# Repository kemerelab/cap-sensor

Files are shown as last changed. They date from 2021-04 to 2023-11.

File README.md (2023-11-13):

# Capacitive sensor
## Theory
Capacitive sensing relies on, as the name suggests, the capacitance of the involved circuit. Capacitance, in turn, is the ability to store electrical charge under an applied voltage, which is employed by components termed capacitors. Clasically, capacitors can be visualized as two conductor plates separated by some distance $d$; the capacitance of these "parallel plate capacitors" is then governed by the equation:

$$
\displaystyle
C = \dfrac{Q}{V} = \epsilon \dfrac{A}{d}
$$

where $Q$ is the electrical charge stored on conductor plate; $V$ is the voltage applied to the capacitor; $\epsilon$ is the dielectric constant of the medium separating the plates; $A$ is the area of each plate; and $d$ is the distance between the plates.

Once charged after application of a voltage across the conductor plates (by, for example, a battery), the capacitor will similarly discharge across another component of a circuit if provided the opportunity. For example, consider the simple RC circuit below.

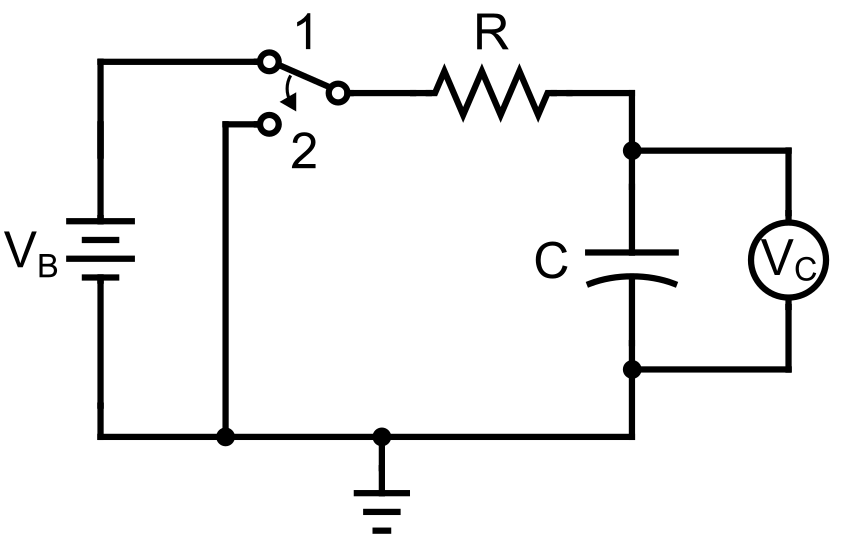
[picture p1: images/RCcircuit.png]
A simple RC circuit.


When connected to the battery, the capacitor with capacitance $C$ will store an amount of charge $Q$ after equilibrating at the battery voltage $V_B$ (position 1). If the circuit is disconnected from the battery (position 2), then an electric current will flow from the positively charged capacitor plate across the resistor to ground. The time-dependent voltage across the capacitor, $V_C$ follows a well-known exponential decay:

$$
\displaystyle
V(t) = V_B e^{-\frac{t}{\tau}}
$$

where $\tau = RC$ is known as the time constant of the circuit and is given by the product of the resistance and capacitance. (Similarly, reflecting the equation across the time axis gives the time-dependence for charging the capacitor.)

Lastly, it can be shown that for capacitors placed in parallel in an electrical circuit, the capacitance of the circuit is the sum of the individual capacitances of each capacitor:

$$
\displaystyle
C_{tot} = C_1 + C_2 + \cdots + C_n
$$

In other words, capacitance is additive in parallel.

How do these principles apply to capacitive sensing? Let's suppose that we have the RC circuit similar to the one above, except that we have an additional wire that connects the positive terminal to a conductive plate (i.e. one-half of a parallel plate capacitor). As some object object, say a finger, approaches this plate, it can form the other (negative) plate to generate an additional parallel plate capacitor. Moreover, if this object is connected to a large electrical reservoir, like a human body, it is in effect "virtually grounded", which functionally acts as if connected to the circuit ground, and thereby makes the new capacitor lie in parallel with the known capacitor. Consequently, because capacitance adds in parallel, the new capacitance of the circuit will have increased. (The exact amount is not important, as we will see.) (If placed directly between the plates of a large capacitor, the sensed object can also affect capacitance by altering the dielectric field; however, this principle is not applicable to this setup.)

How do we measure this change in capacitance? By relying on the time constant of the RC circuit! After charging the capacitor(s), the battery is disconnected, and the rate of voltage decay across the capacitor can be measured. As the sensed object (finger) approaches the sensor (plate), the overall capacitance of circuit increases. Because the resistance is fixed, the time constant is only modified by the change in capacitance and consequently increases as well. Thus, the time for the voltage to decrease by a given amount is prolonged. (We could similarly measure the time to charge the capacitor and see that it is also prolonged with increased capacitance.)

Although the voltage change during discharge theoretically follows an exponential decay, it often not necessary to model the voltage decay as such, nor to solve for $\tau$ directly. As mentioned above, the change in capacitance will alter the time to reach certain voltage thresholds during discharge in a predictable direction. The codebase on which this sensor is based counts the number of cycles on the microcontroller until logic LOW is reached as a rough estimate of this duration. An increase or decrease in this output reflects an increase or decrease, respectively, of the circuit capacitance.

The implementation of capacitive sensing for lick detection is shown below. An RC circuit is run on a microcontroller that toggles between charging (position 1) and discharging (position 2) the integrated capacitor ($C_1$). Additionally, a wire connects the positive terminal to the metallic lick spout, which functions as one end of a capacitor. During licking, as the tongue approaches the lick spout, it functions as the other end of the capacitor ($C_2$), thereby increasing the capacitance of the RC circuit and, consequently, the time constant, a detectable change as noted above. The tongue is connected to the animal's body and perhaps, depending on the specifics of the experimental rig, the material on which the animal is sitting; in either case, the electrical storage capacity is large enough relative to the circuit that it functions as a virtual ground for the "other" plate of the capacitor. (Although the tongue does touch the lick spout during licking, the specifics of whether the sensor is detecting proximity or contact is less important. For instance, even when in contact with the lick spout directly, the intervening reward solution and saliva, as well as the epithelial layer of the tongue, can be modeled as the dielectric material separating the capacitive plates for a capacitor, albeit a potentially leaky one.) 

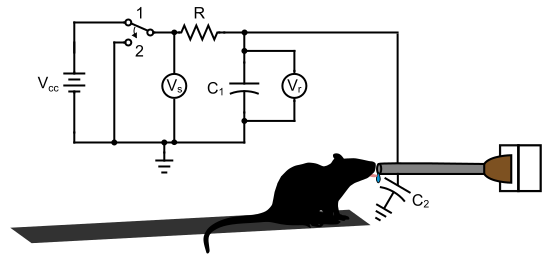
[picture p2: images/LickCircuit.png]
Implementation of capacitive sensing for lick detection.


The change in charging or discharging time in the RC circuit is detected by a script running on the microcontroller. Both a "send" pin and a "receive" pin are initially set to logic LOW in an output state. The send pin is then switched to logic HIGH ($V_s$), while the receive pin is switched to an input state. A counter tracks the number of clock cycles until the voltage of the recieve pin ($V_r$) reaches the logic HIGH state (i.e. capacitor charging). Once the capacitor is fully charged, the reverse occurs to track capacitor discharging. Full implementation details can be found at the developers' repository [here](https://github.com/PaulStoffregen/CapacitiveSensor).

## Overview of sensor
### Hardware
The capacitive sensing components are integrated onto a small printed circuit board (PCB) that was designed using Autodesk EAGLE (v9.5). Files pertaining to the PCB, including design files and parts lists, can be found in the `pcb` directory. A schematic is shown below.

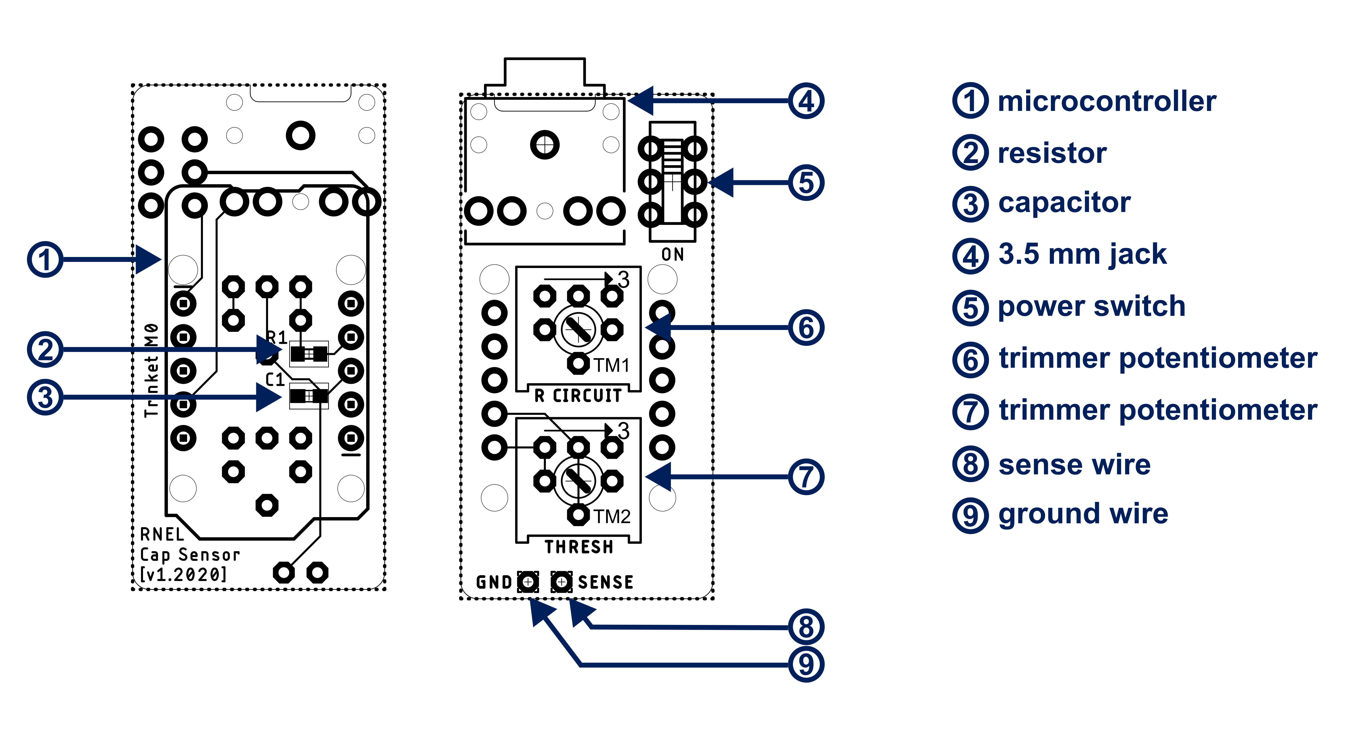
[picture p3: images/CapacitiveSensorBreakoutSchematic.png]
Schematic of sensor PCB.


The sensor uses a microcontroller (Adafruit M0 Trinket; component **1** in diagram) that gathers the sensing input, runs the lick detection firmware (more below), and outputs the lick signal. It requires a 3.3V power source (but is tolerant up to 6V) that may be provided either directly through the micro USB hub or through the audio jack (**4**) via an external source that may be switched on or off (**5**). The components of the sensing circuit are the thru-hole for a wire connected to the lickspout (**8**); a fixed (**2**) and variable (**6**) resistor (comprising $R$ in circuit diagram above); a stabilizing capacitor (**3**, comprising $C_1$ in diagram above); and, if needed, a thru-hole for a separate ground connection (**9**). The voltage from this modified RC circuit is fed as input into a pin on the microcontroller in order to run lick detection firmware. The sensitivity of lick detection can be adjusted manually by tuning the specified variable resistor (**7**).

The output signal is sent via a different microcontroller pin to the signal component (ring of tip-ring-sleeve, or TRS, composition) of the audio jack. Additionally, the red status LED turns on whenever a lick is detected (i.e. HIGH signal output).

### Firmware
The firmware that runs lick detection can be found under the `firmware` directory. Three different scripts (`capacitiveSensor`, `capacitiveSensorFilter`, `capacitiveSensorVariable`) run a common algorithm with slightly different variants. The input voltage from the lick detection circuit is fed to the [CapacitiveSensor](https://github.com/PaulStoffregen/CapacitiveSensor) library to provide a rough estimate of the time constant, which is returned as a unitless number. Larger values mean larger time constants and a higher likelihood of a lick occurring. Once the value exceeds a set threshold, a lick is detected and the signal output set to HIGH. That threshold can be fixed in the firmware (`capacitiveSensor.ino`) or modified within a range by the variable resistor knob on the PCB (`capacitiveSensor.ino`). Lastly, the time constant values instead may be first fed through a filter (`capacitiveSensorFilter.ino`; moving average or median filter) in order to smooth the input signal. Explanations of the parameters within and use of each script is provided below in `Usage Guide`.

## Installation
The PCB design files and a list of hardware components can be found in the `pcb` directory. Once acquired, the surface-mount (R1, C1) and through-hole (trimpots, power switch, audio jack) components should be soldered to the PCB. Pin headers should be soldered to the PCB and to the microcontroller, which can be then be mounted onto the board.

Next, an insulated wire should be measured and cut to the desired length, noting that it will be connected to the through-hole labeled `SENSE` at one end and to the lickspout at the other. The length of wire should allow for enough slack to avoid pulling on either component but avoid excess slack, which will increase the noise of the input (as it essentially functions as an antenna). We suggest first soldering the wire to the lickspout and then soldering the other end to the through-hole.

After all components have been soldered to the board, the microcontroller should be programmed with the firmware of choice. A computer containing the firmware files can be connected to the microcontroller via its micro USB hub. Either the Arduino IDE (which can be downloaded [here](https://www.arduino.cc/en/software)) or software with Arduino integration (e.g. VS Code) may be used to upload the firmware. A detailed guide to installing the IDE and uploading scripts can be found [here](https://learn.adafruit.com/adafruit-trinket-m0-circuitpython-arduino/arduino-ide-setup). The three scripts that may be uploaded are `capacitiveSensor.ino`, `capacitiveSensorFilter.ino`, and `capacitiveSensorVariable.ino`. If using `capacitiveSensorFilter.ino`, the binaries for the files located in `firmware/libaries` must be compiled to a location within `firmware` (such as `firmware/bin`).

Once the hardware and firmware installation is complete, the microcontroller may be powered by either the audio jack via an external power supply or the microUSB port. In either case, it requires a 3.3 V power supply but is tolerant up to 6 V. If the audio jack is used, the power and ground should be connected to the tip and sleeve of the cable, respectively. Note that if the microUSB port is connected to a host computer, then power will automatically switch over even if an external power source is connected to the audio jack.

The output signal may be harnessed from either pin 3 on the microcontroller or the ring component of the audio jack. The output is logic LOW when no lick is detected and logic HIGH when a lick is detected.

## Usage guide
The sensor may be quickly tested by touching the peripheral end of the sense wire or the component to which it is connected (e.g. a lickspout). The red status LED on the microcontroller should turn on when the component is touched and only when it is touched. If the status light does not illuminate, first attempt to modify the settings below before proceeding to the Troubleshooting section.

As with many sensors, there is a trade-off between the sensitivity (capturing lick events) and specificity (ignoring noise) of detection, of which the sensor has two primary means of adjusting: via hardware and via firmware.

The knob on the variable resistor (trimpot) labeled `R CIRCUIT` tunes the resistance of the RC circuit that underlies lick detection. By turning it clockwise, the resistance is increased, which in turn increases the sensitivity of the detector. (Specifically, the time constant is increased via the $R$ in $\tau=RC$; any changes in the capacitance $C$ are then amplified in the read-out value on which detection is thresholded.) Larger values may reliably detect proxmity rather than touch if desired.

Each script has modifiable parameters that govern its sensitivity to lick detection. The most straightforward is the detection threshold, which, using output values from the underlying `CapacitiveSensor` library, delineates between the baseline state (below threshold) and lick state (above threshold). The detection threshold may be hard-coded (in `capacitiveSensor.ino`) or adjusted via the knob on the trimpot labeled `THRESH` (in `capacitiveSensorVariable.ino` and `capacitiveSensorFilter.ino`). In the latter case, the range of values corresponding to the knob position are set by the low and high limits coded in the script. All scripts are specify the sampling rate, which corresponds to the frequency with which sensor values are sampled and compared to threshold. If filters are employed (`capacitiveSensorFilter.ino`), several other parameters specify various properties of the filter that affect detection speed and accuracy; these are explained in further detail in the iPython notebook found at `testing/python/filters.ipynb`. The full list of parameters is displayed in the table below.

| parameter | variable name | description | script(s) |
|-----------|---------------|-------------|-----------|
| sampling rate | `sampleRate` | rate of sensor value acquisition | `capactiveSensor`, `capactiveSensorVariable`, `capactiveSensorFilter` |
| threshold | `th`, `thresh` | value above which the output signal is HIGH | `capactiveSensor`, `capactiveSensorVariable`, `capactiveSensorFilter` |
| lower limit of threshold | `th_low`, `thresh_low` | threshold value when `THRESH` set to lowest setting | `capactiveSensorVariable`, `capactiveSensorFilter` |
| upper limit of threshold | `th_high`, `thresh_high` | threshold value when `THRESH` set to highest setting | `capactiveSensorVariable`, `capactiveSensorFilter` |
| algorithm sensitivity | `sensitivity` | number of cycles to estimate time constant | `capactiveSensorFilter` |
| threshold type* | `method` | specifies threshold based on absolute values or z-score | `capactiveSensorFilter` |
| coefficient of signal value* | `alpha` | contribution of signal to filter buffer stats | `capactiveSensorFilter` |
| filter duration* | `tFilter` | duration of filter buffer (seconds) | `capactiveSensorFilter` |
| downsample factor* | `k` | specifies period for updating filter buffer |  `capactiveSensorFilter` |

*See `testing/python/filters.ipynb` for details.

## Troubleshooting
**General debugging**: Each firmware script is programmed to output debugging values every iteration as listed in the table below. When the microcontroller is connected to a host computer via its microUSB hub, these values can be accessed either through the serial monitor or by piping the output to a text file. Each row represents values for a given iteration, and values within an iteration are separated by a whitespace.

| firmware | default frequency | values | | | | |
|---|---|---|---|---|---|---|
`capactiveSensor` | 30 kHz | timestamp (microseconds) | sensor value | | | |
`capacitiveSensorVariable` | 30 kHz | timestamp (microseconds) | sensor value | detection threshold | | |
`capacitiveSensorFilter` | 0.2 kHz | timestamp (microseconds) | sensor value | detection threshold | buffer mean | output |

**Error occurs while attempting to upload firmware**: Make sure that both the Adafruit and the Arduino libraries for the SAMD21 boards are installed in board config (see tutorial [here](https://learn.adafruit.com/adafruit-trinket-m0-circuitpython-arduino/arduino-ide-setup)).

**Microcontroller not recognized by computer (i.e. does not mount)**: Try resetting the microcontroller by (1) double clicking the reset button on the microcontroller to enter bootloader mode (red LED should flash on and off), and then (2) dragging the appropriate UF2 file into the newly mounted controller (see [here](https://learn.adafruit.com/introducing-itsy-bitsy-m0/uf2-bootloader-details) for details).

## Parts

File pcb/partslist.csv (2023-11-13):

Name | Part | Value | Manufacturer | Product ID | Description
capacitor (0603 SMD) | C1 | 100pF | - | - | provides baseline capacitance in sensor circuit
resistor (0603 SMD) | R1 | 501k | - | - | provides baseline resistance in sensor circuit
trimpot | TM1 | 1M | Bourns | 3386P-1-105TLF | tunes resistance in sensor circuit
trimpot | TM2 | 5k | Bourns | 3386P-1-502TLF | tunes detection threshold in firmware
audio jack | J1 | 3.5 mm | CUI Devices | SJ1-3523N | carries power, signal output, and ground
power switch | SWITCH | DPDT | C&K | JS202011CQN | power switch for PCB
microcontroller | JP5/JP6 | Trinket M0 | Adafruit | 3500 | runs firmware for signal detection

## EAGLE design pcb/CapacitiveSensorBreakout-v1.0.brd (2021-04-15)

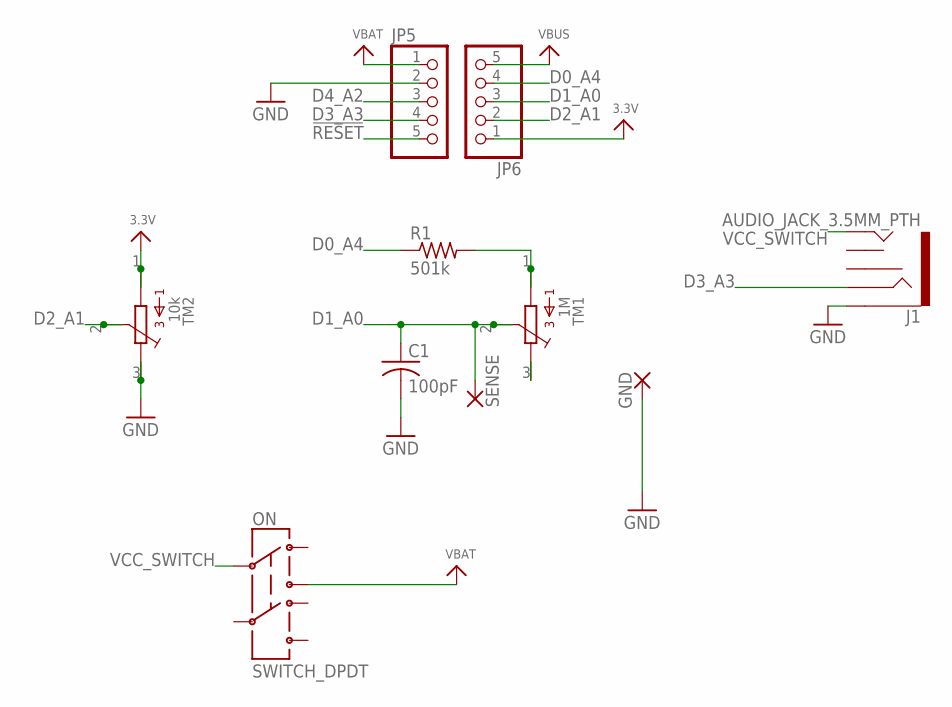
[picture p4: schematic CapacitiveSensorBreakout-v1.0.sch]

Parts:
C1: 100pF; C0603
GND: 1,6/0,8
J1: AUDIO_JACK_3.5MM_PTH; AUDIO-JACK
JP5, JP6: HEADER-1X576MIL; 1X05_ROUND_76
ON: SWITCH_DPDT; JS_DPDT_TH
R1: 501k; R0603
SENSE: 1,6/0,8
TM1: 1M; 3386-MULTI
TM2: 10k; 3386-MULTI

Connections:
3.3V: JP6.1, TM2.1, TM2.4
!RESET: JP5.5
D0_A4: JP6.4, R1.1
D1_A0: C1.1, JP6.3, SENSE.1, TM1.2, TM1.5
D2_A1: JP6.2, TM2.2, TM2.5
D3_A3: J1.RING, JP5.4
D4_A2: JP5.3
GND: C1.2, GND.1, J1.SLEEVE, JP5.2, TM2.3, TM2.6
unnamed: TM1.3, TM1.6
unnamed: R1.2, TM1.1, TM1.4
VBAT: JP5.1, ON.3
VBUS: JP6.5
VCC_SWITCH: J1.TIP, ON.2

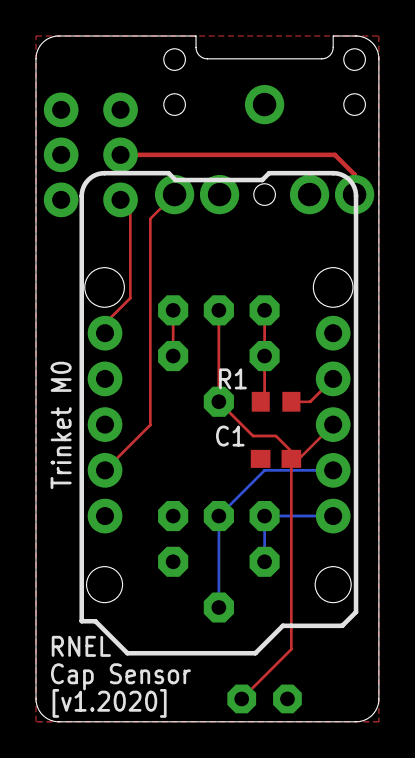
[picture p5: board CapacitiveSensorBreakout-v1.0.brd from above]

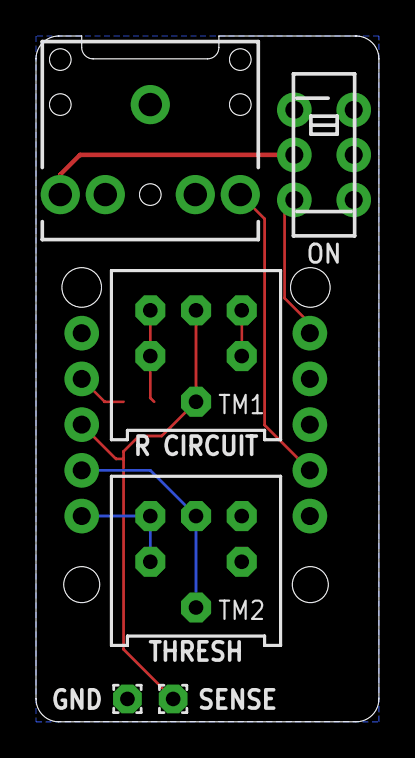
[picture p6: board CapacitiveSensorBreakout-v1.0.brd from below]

Board: 2 copper layers, 19.1 x 38.1 mm, 10 parts (6 on the bottom side), 10 nets.

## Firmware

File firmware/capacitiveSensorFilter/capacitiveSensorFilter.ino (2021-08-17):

#include <CapacitiveSensor.h>
#include <filter.h>

// Settings
const int nSensors = 1; // number of lick sensors
long sensitivity = 30; // sensor sensitivity (increases acquisition time)
bool hasAnalogPin = true; // does setup use analog input pin to determine threshold?
char method = 'A'; // 'A' = use absolute threshold, 'S' = use std threshold
double thresh; // threshold for detecting lick (stds from mean or raw value)
double thresh_low = 500.0; 
double thresh_high = 10000.0;
double alpha = 0.000; // contribution of signal to filter buffer stats
double tFilter = 20.0; // duration of filter buffer (s) (determines responsiveness)
double sampleRate = 200.0; // sample frequency (Hz) (determines resolution)
long k = 10; // downsample factor; update buffer every k samples

// Sensor I/O (constructor format: (pin_HIGH, pin_LOW))
CapacitiveSensor cs[] = {CapacitiveSensor(0, 1)};
long val; // sensor value
int pinsOut[nSensors] = {3}; // output pins
int ledsOut[nSensors] = {13}; // LEDs representing sensor states
int output[nSensors]; // current output states
int analogPin = A1; // threshold input

// Sensor filter
MovingFilter mf[nSensors]; // filters
int x; // filter signal

// Timing variables
unsigned long tStart;
unsigned long tCurrent; 
unsigned long samplePeriod; 

// Command setup
const unsigned int MAX_LENGTH = 100;
char cmd[MAX_LENGTH];
unsigned int cmdPointer = 0;

void setup() {
    // Set pins to low voltage
    for (int i = 0; i < nSensors; i++)
    {
        pinMode(pinsOut[i], OUTPUT);
        pinMode(ledsOut[i], OUTPUT);
        digitalWrite(pinsOut[i], LOW);
        digitalWrite(ledsOut[i], LOW);
        output[i] = LOW;
    }

    // Blink LED on/off five times (debugging)
    // for (int j = 0; j < 5; j++) {
    //     for (int i = 0; i < nSensors; i++) {
    //         digitalWrite(ledsOut[i], HIGH);
    //     }
    //     delay(500);
    //     for (int i = 0; i < nSensors; i++) {
    //         digitalWrite(ledsOut[i], LOW);
    //     }
    //     delay(500);
    // }

    // Set analog input for threshold
    if (hasAnalogPin) {
        pinMode(analogPin, INPUT);
        thresh = getThreshold(analogRead(analogPin));
    }
    
    // Begin serial transmission
    Serial.begin(115200);

    // Raise error if 1) sample rate > 0.002 / (nSensors * sensitivity/30), or 
    // 2) buffer size > 1500
    double sampleRateMax = (1.0 / (2.0e-3 * (double) nSensors * ((double) sensitivity / 30.0)));
    if (sampleRate > sampleRateMax) {
        Serial.print("sampleRate of "); Serial.print(sampleRate); 
        Serial.print(" exceeds maximum of "); Serial.println(sampleRateMax);
        Serial.print("Changing sampleRate to "); Serial.println(sampleRateMax);
        sampleRate = sampleRateMax;
    }
    long n = (long) (tFilter * sampleRate / (double) k);
    int nMax = (long) (1500.0 / ((double) nSensors));
    if (n > nMax) {
        Serial.print("buffer size of "); Serial.print(n); 
        Serial.print(" exceeds maximum of "); Serial.println(nMax);
        Serial.print("Changing buffer size to "); Serial.println(nMax);
        n = nMax;
    }

    // Create filters
    for (int i = 0; i < nSensors; i++) {
        mf[i].createFilter(n, k, thresh, alpha, method);
    }

    // Get start time and minimum sample period
    tStart = micros(); // time in ms
    samplePeriod = (unsigned long) ((1.0/sampleRate)*1e6); // period in us 

    // Print parameters before beginning loop
    Serial.println("Starting sensor with parameters:");
    Serial.print("buffer size: "); Serial.println(n);
    Serial.print("buffer duration: "); Serial.println((double) n * samplePeriod * 1.0e-6 * (double) k);
    Serial.print("buffer update rate: "); Serial.println(sampleRate / (double) k);
    Serial.print("sample rate: "); Serial.println(sampleRate);
    Serial.print("alpha: "); Serial.println(alpha, 5);
    if (hasAnalogPin) {
        Serial.print("signal threshold range: "); Serial.print(thresh_low, 2); Serial.print(" - "); Serial.println(thresh_high, 2);
    }
    else {
        Serial.print("signal threshold: "); Serial.println(thresh, 2);
    }
    Serial.println();
}

void loop() {
    // Get time
    tCurrent = micros();
    
    // Check command
    // TODO: freezes with Trinket M0 for some reason...
    // if (Serial.available() > 0) {
    //     processCommand();
    // }

    // Write sensor value with sample frequency or if clock restarted
    if ((tCurrent - tStart > samplePeriod) || (tCurrent - tStart < 0))
    {
        //Serial.print(tCurrent);
        Serial.print(tCurrent);

        for (int i = 0; i < nSensors; i++)
        {
            // Get current sensor value
            // Note: sensor value acquisition limits transmission rate
            val = cs[i].capacitiveSensorRaw(sensitivity); // use raw value to avoid heuristic conflicting with filter
      
            // Print raw values
            Serial.print(" ");
            Serial.print(val);

            // Get current threshold and update filter
            if (hasAnalogPin) {
                thresh = getThreshold(analogRead(analogPin));
                mf[i].thresh = thresh;
            }

            // Print threshold value
            Serial.print(" ");
            Serial.print(thresh);

            // Print buffer mean (baseline)
            Serial.print(" ");
            Serial.print(mf[i].bufferMean());

            // Get filtered values
            x = mf[i].applyFilter((double) val);

            // NOTE: Do not call reset() after a "negative" signal! This will
            // cause many timeouts within a lick bout as the negative component
            // of the fluctuation may exceed threshold and thus call the reset()
            // function often, which triggers a delay as the buffer refills.
            //if (x == -1) {
            //    mf[i].reset();
            //}
      
            // Print filtered values
            Serial.print(" ");
            Serial.print(x);
            
            // Write digital I/O if threshold crossed
            if ((x == 1) && (output[i] == LOW))
            {
                digitalWrite(pinsOut[i], HIGH);
                digitalWrite(ledsOut[i], HIGH);
                output[i] = HIGH;
            }
            else if ((x < 1) && (output[i] == HIGH))
            {
                digitalWrite(pinsOut[i], LOW);
                digitalWrite(ledsOut[i], LOW);
                output[i] = LOW;
            }
        }
    Serial.print("\n");
    tStart = tCurrent;
  }
}

void processCommand(void) {
  // Add char to buffer
  char c = Serial.read();
  
  // Process command if newline; otherwise, add to char array
  if (c == '\n') {
    // Find whitespace to separate command name and value
    int j;
    for (int i = 0; i < cmdPointer; i++) {
      if (cmd[i] == ' ') {
        j = i;
        break;
      }
    }

    // Parse command name and value
    char name[j+1];
    memcpy(name, &cmd, j*sizeof(*cmd));
    name[j] = '\0';
    char val[cmdPointer-j];
    memcpy(val, &cmd[j+1], (cmdPointer-j-1)*sizeof(*cmd));
    val[cmdPointer-j-1] = '\0';

    // Set new value
    if (strcmp(name, "alpha") == 0) {
      alpha = atof(val);
      Serial.print("Setting alpha to "); Serial.println(alpha, 5);
      for (int i = 0; i < nSensors; i++) {
        mf[i].alpha = alpha;
      }
      delay(5000);
    }
    else if (strcmp(name, "thresh") == 0) {
      thresh = atof(val);
      Serial.print("Setting threshold to "); Serial.println(thresh, 2);
      for (int i = 0; i < nSensors; i++) {
        mf[i].thresh = thresh;
      }
      delay(5000);
    }
    else {
      Serial.print("Unknown command: ");
      Serial.println(cmd);
    }

    // Update command variables
    cmdPointer = 0;
  }
  else {
    // add to cmd
    if (cmdPointer < MAX_LENGTH) {
      cmd[cmdPointer] = c;
      cmdPointer++;
    }
    else {
      Serial.println("Maximum command length exceeded.");
      cmdPointer = 0;
    }
  }
}

float getThreshold(int val) {
    // analogRead() range 0-1023 (10-bit ADC)
    //return (long) ((float(val)/1023)*(thresh_high - thresh_low) + thresh_low); // directly proportional
    return (long) ((1.0 - (float(val)/1023))*(thresh_high - thresh_low) + thresh_low); // inversely proportional
}

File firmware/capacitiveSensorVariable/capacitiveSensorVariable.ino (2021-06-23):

#include <CapacitiveSensor.h>

// Settings
int nSensors = 1; // number of lick sensors
long th; // threshold for detecting lick
float th_low = 10.0;
float th_high = 10000.0;
float sampleRate = 30000.0; // rate to print to serial

// Sensor I/O (constructor format: (pin_HIGH, pin_LOW))
CapacitiveSensor cs[] = {
  CapacitiveSensor(0, 1)
};
long vals[1]; // sensor values
int pinsOut[1] = {3}; // output pins
int ledsOut[1] = {13}; // LEDs representing sensor states
int output[1] = {LOW}; // current output states
int analogPin = A1; // threshold input

// Timing variables
unsigned long tStart;
unsigned long tCurrent; 
unsigned long samplePeriod; 

void setup() {
  // Set pins to low voltage
  for (int i = 0; i < nSensors; i++)
  {
    pinMode(pinsOut[i], OUTPUT);
    pinMode(ledsOut[i], OUTPUT);
    digitalWrite(pinsOut[i], LOW);
    digitalWrite(ledsOut[i], LOW);
  }

  // Set analog input for threshold
  pinMode(analogPin, INPUT);

  // Begin serial transmission
  Serial.begin(115200);
  
  // Get start time and minimum sample period
  tStart = micros(); // time in ms
  samplePeriod = (unsigned long) ((1.0/sampleRate)*1e6); // period in us
}

void loop() {
  // Get current sensor value and time
  // Note: sensor value acquisition limits transmission rate
  tCurrent = micros();
  Serial.print(tCurrent);
  for (int i = 0; i < nSensors; i++)
  {
    vals[i] = cs[i].capacitiveSensor(30);
  }
    
  // Get current threshold
  th = getThreshold(analogRead(analogPin));

  // Write sensor value with sample frequency or if clock restarted
  if ((tCurrent - tStart > samplePeriod) || (tCurrent - tStart < 0))
  {
    for (int i = 0; i < nSensors; i++)
    {
      Serial.print(" ");
      Serial.print(vals[i]);
    }
    Serial.print(" ");
    Serial.print(th);
    Serial.print("\n");
    tStart = tCurrent;
  }
  
  // Write digital I/O if threshold crossed
  for (int i = 0; i < nSensors; i++)
  {
    if ((vals[i] > th) && (output[i] == LOW))
    {
      digitalWrite(pinsOut[i], HIGH);
      digitalWrite(ledsOut[i], HIGH);
      output[i] = HIGH;
    }
    else if ((vals[i] < th) && (output[i] == HIGH))
    {
      digitalWrite(pinsOut[i], LOW);
      digitalWrite(ledsOut[i], LOW);
      output[i] = LOW;
    }
  }
}

float getThreshold(int val) {
  // analogRead() range 0-1023 (10-bit ADC)
  //return (long) ((float(val)/1023)*(th_high - th_low) + th_low); // directly proportional
  return (long) ((1.0 - (float(val)/1023))*(th_high - th_low) + th_low); // inversely proportional
}

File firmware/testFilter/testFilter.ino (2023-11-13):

#include <CapacitiveSensor.h>
#include <filter.h>

// To test the filter code, change `#include <math.h>` to `#include <cmath>` 
// in `filter.cpp`, and compile `medianFilter.cpp` and/or `movingFilter.cpp`.

// Settings
const int nSensors = 2; // number of lick sensors
long sensitivity = 120; // sensor sensitivity
double thresh = 4.0; // threshold for detecting lick (stds from mean)
double alpha = 0.0; // contribution of signal to filter buffer stats
double tFilter = 0.25; // duration of filter buffer (s) (determines responsiveness)
double sampleRate = 500.0; // sample frequency (Hz) (determines resolution)

// Raise error if 1) buffer size > 1500 or 2) sample rate > 500 / nSensors

// Sensor I/O (constructor format: (pin_HIGH, pin_LOW))
CapacitiveSensor cs[] = {
  CapacitiveSensor(13, 11),
  CapacitiveSensor(4, 2)
};
long val; // sensor value
int pinsOut[nSensors] = {22, 23}; // output pins
int output[nSensors]; // current output states

// Sensor filter
long n = (long) (tFilter * sampleRate);
MovingFilter mf[] = {
  MovingFilter(n, thresh, alpha),
  MovingFilter(n, thresh, alpha)
};
int x; // filter signal

// Timing variables
unsigned long tStart;
unsigned long tCurrent; 
unsigned long samplePeriod; 

// Command setup
const unsigned int MAX_LENGTH = 100;
char cmd[MAX_LENGTH];
unsigned int cmdPointer = 0;

void setup() {
  // Set pins to low voltage
  for (int i = 0; i < nSensors; i++)
  {
    pinMode(pinsOut[i], OUTPUT);
    digitalWrite(pinsOut[i], LOW);
    output[i] = LOW;
  }

  // Begin serial transmission
  Serial.begin(115200);
  Serial.println(n);
  
  // Get start time and minimum sample period
  tStart = micros(); // time in ms
  samplePeriod = (unsigned long) ((1.0/sampleRate)*1e6); // period in us 
  Serial.println(samplePeriod);
}

void loop() {
  // Get time
  tCurrent = micros();
  
  // Check command
  if (Serial.available() > 0) {
    processCommand();
  }

  // Write sensor value with sample frequency or if clock restarted
  if ((tCurrent - tStart > samplePeriod) || (tCurrent - tStart < 0))
  {
    //Serial.print(tCurrent);
    Serial.print(tCurrent - tStart);

    for (int i = 0; i < nSensors; i++)
    {
      // Get current sensor value
      // Note: sensor value acquisition limits transmission rate
      val = cs[i].capacitiveSensor(sensitivity);
      
      // Print raw values
      Serial.print(" ");
      Serial.print(val);

      // Get filtered values
      x = mf[i].applyFilter((double) val);
      if (x == -1) {
        mf[i].reset();
      }
      
      // Print filtered values
      Serial.print(" ");
      Serial.print(x);
      // Further debugging
      // NOTE: These class variables must be made public in
      // the header file to be printed here.
      /*
      Serial.print(" ");
      Serial.print(mf[i].mean);
      Serial.print(" ");
      Serial.print(mf[i].std);
      Serial.print(" ");
      Serial.print(mf[i].t);
      Serial.println();
      for (int j = 0; j < 10; j++) {
        Serial.print(mf[i].buffer[j]);
        Serial.print(" ");
      }
      Serial.print("\n");
      */
      
      // Write digital I/O if threshold crossed
      if ((x == 1) && (output[i] == LOW))
      {
        digitalWrite(pinsOut[i], HIGH);
        output[i] = HIGH;
      }
      else if ((x < 1) && (output[i] == HIGH))
      {
        digitalWrite(pinsOut[i], LOW);
        output[i] = LOW;
      }
    }
    Serial.print("\n");
    tStart = tCurrent;
  }
  
}
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

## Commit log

2021-04-15 added breakout board files
    [CapacitiveSensorBreakout-v1.0.brd, CapacitiveSensorBreakout-v1.0.sch]
2021-04-21 added correct output pin for Trinket M0
2021-05-14 updated filtered version to be compatible with Trinket M0 breakout board
2021-08-17 new experimental and filtered data files
2021-08-17 experimental data analysis of appropriate filters for estimating baseline
2023-11-13 updated documentation
    [partslist.csv]

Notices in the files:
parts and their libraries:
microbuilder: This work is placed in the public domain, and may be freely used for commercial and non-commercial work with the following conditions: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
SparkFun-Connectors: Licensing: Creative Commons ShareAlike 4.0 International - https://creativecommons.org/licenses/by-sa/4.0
